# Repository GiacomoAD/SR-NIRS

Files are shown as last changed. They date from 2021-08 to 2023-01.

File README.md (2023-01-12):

# SR-NIRS
> Started on Jan/2021

SR-NIRS is a project to develop a low cost, portable, Spatially Resolved Near-Infrared Spectroscopy embedded system. Currently, the project is based on ESP-32 microcontroller.

The goal is to be able to monitor Tissue Oxygenation Index (TOI) from the forearm muscle during arm arterial occlusion experiment in a real time application.

The project also includes the development of a *Python GUI* to interact with the system.

*Undergraduate Final Project*

## Python GUI

This system was developed along with a Python GUI to enable wireless (currently Bluetooth) communication and data logging, as well as user monitoring of the incoming NIRS signal.

****

### Setup - Python Virtual Environment  

**This step, even though recommended, is not required. You can skip to Python Requirements sections if you wish.**

First of all, it is recommended to create a Python Virtual Environment. This can be done through python's embedded  (v. 3.4+) module called **venv**:

```
python -m venv [directory]
``` 

Then, the environment should be activated through:  
- ### Windows  
``` 
[directory]\Scripts\activate.bat
```

- ### Linux or MacOS  
```
source [directory]/bin/activate 
``` 

[More information on python virtual environments can be found here.](https://python.land/virtual-environments/virtualenv)

### Setup - Python Requirements

All of the required packages are included on **_requirements.txt_** file, inside **_GUI_** folder.  

These requirements can be installed through python's **pip** module, as it follows:

```
pip install -r requirements.txt
``` 

### Running GUI

To run the system GUI, the **_main.py_** script should be executed:
```
python main.py
``` 

***
## Documentation

The documentation will be in included in this repository as the project progresses.

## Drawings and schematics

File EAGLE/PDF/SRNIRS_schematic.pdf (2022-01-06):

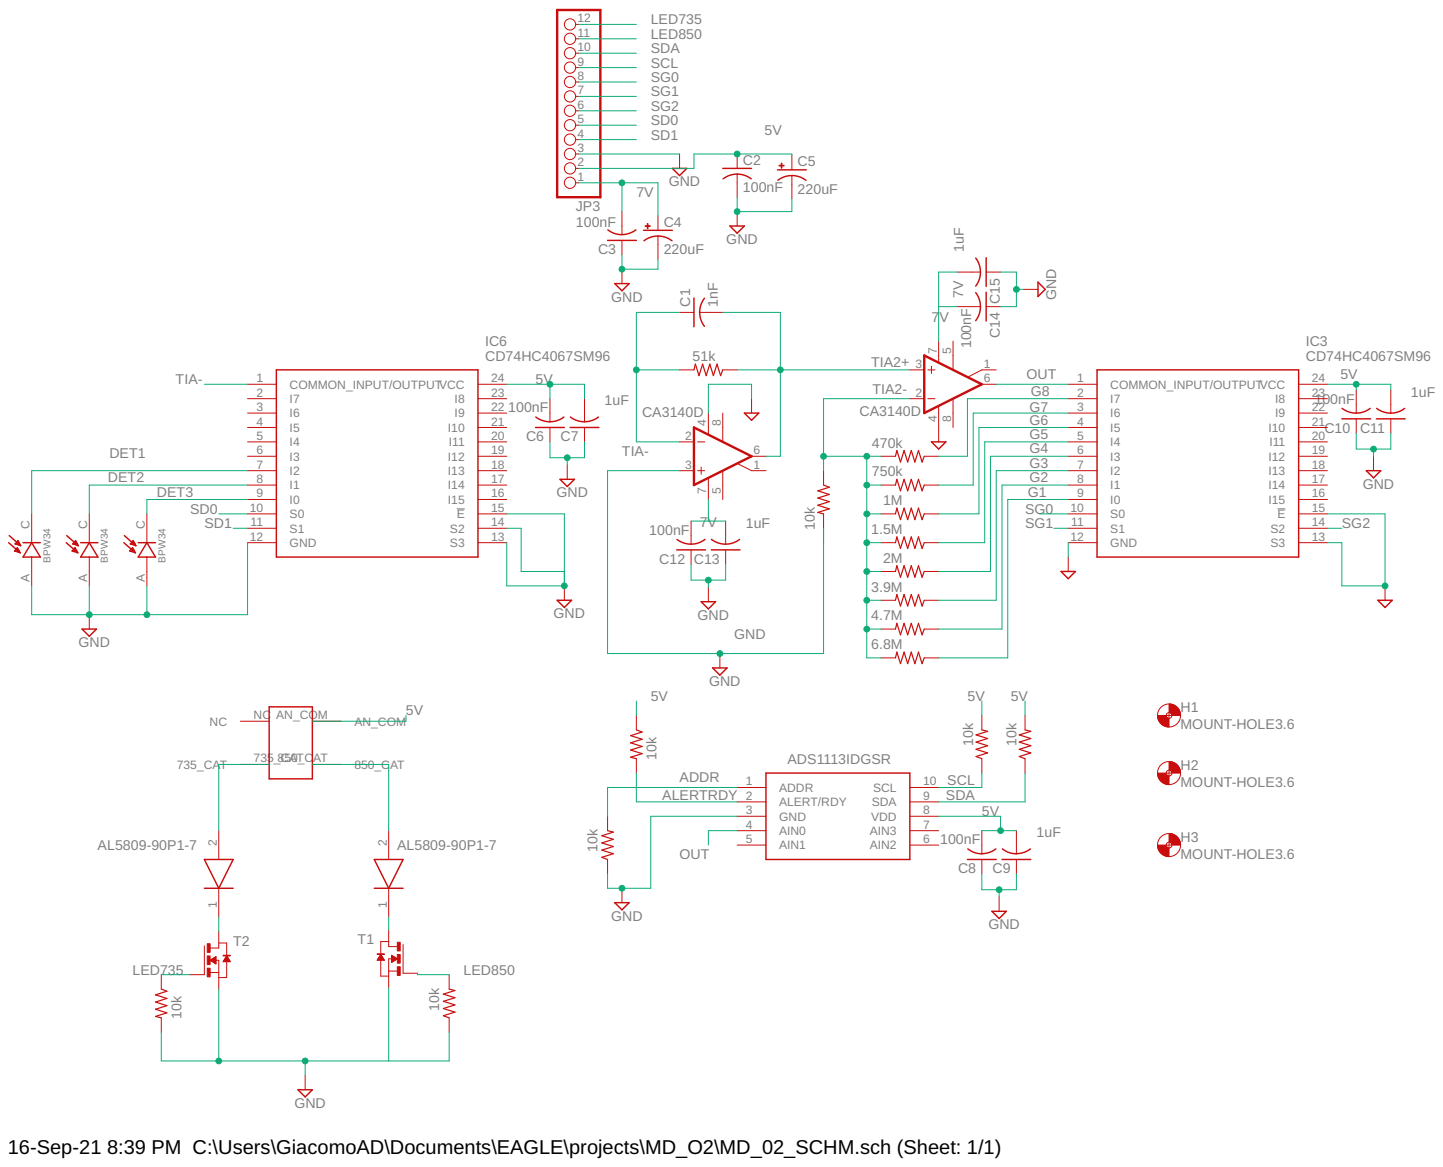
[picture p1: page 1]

16-Sep-21 8:39 PM C:\Users\GiacomoAD\Documents\EAGLE\projects\MD_O2\MD_02_SCHM.sch (Sheet: 1/1)

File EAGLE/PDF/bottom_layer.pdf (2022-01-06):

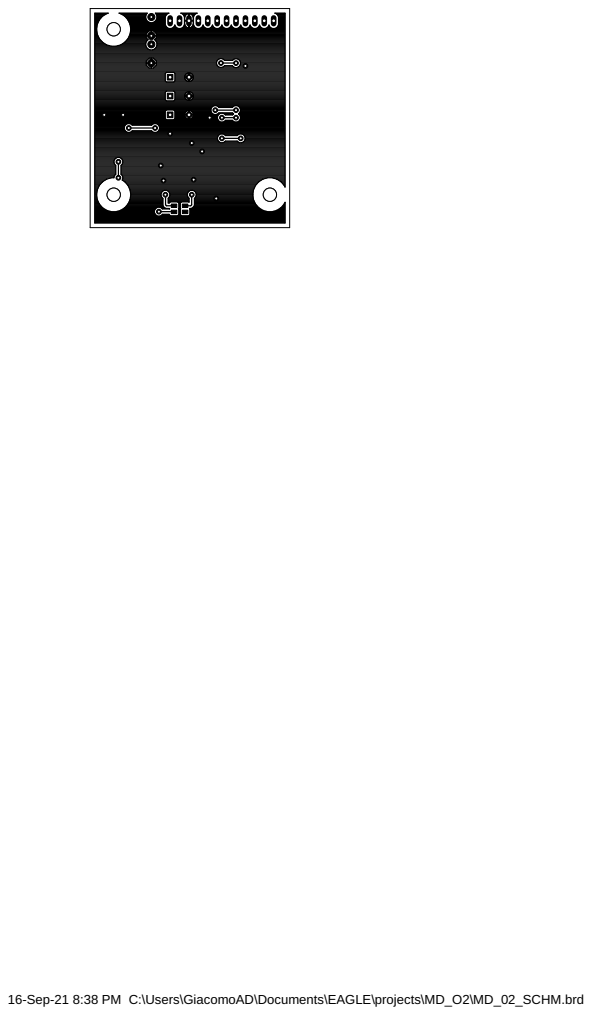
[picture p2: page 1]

16-Sep-21 8:38 PM C:\Users\GiacomoAD\Documents\EAGLE\projects\MD_O2\MD_02_SCHM.brd

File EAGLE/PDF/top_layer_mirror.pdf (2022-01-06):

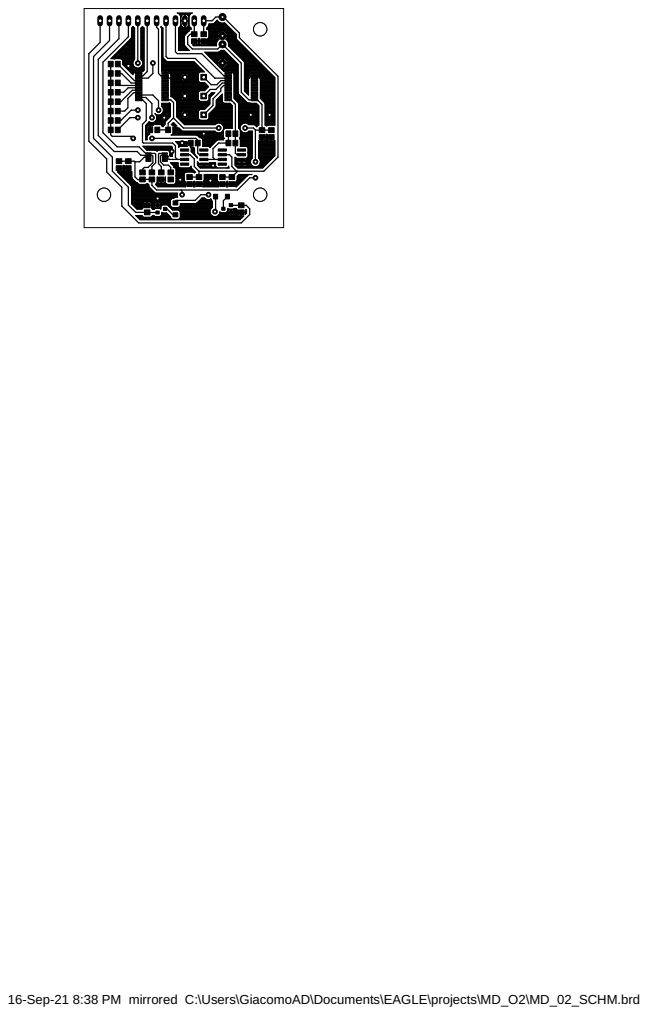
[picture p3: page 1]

16-Sep-21 8:38 PM mirrored C:\Users\GiacomoAD\Documents\EAGLE\projects\MD_O2\MD_02_SCHM.brd

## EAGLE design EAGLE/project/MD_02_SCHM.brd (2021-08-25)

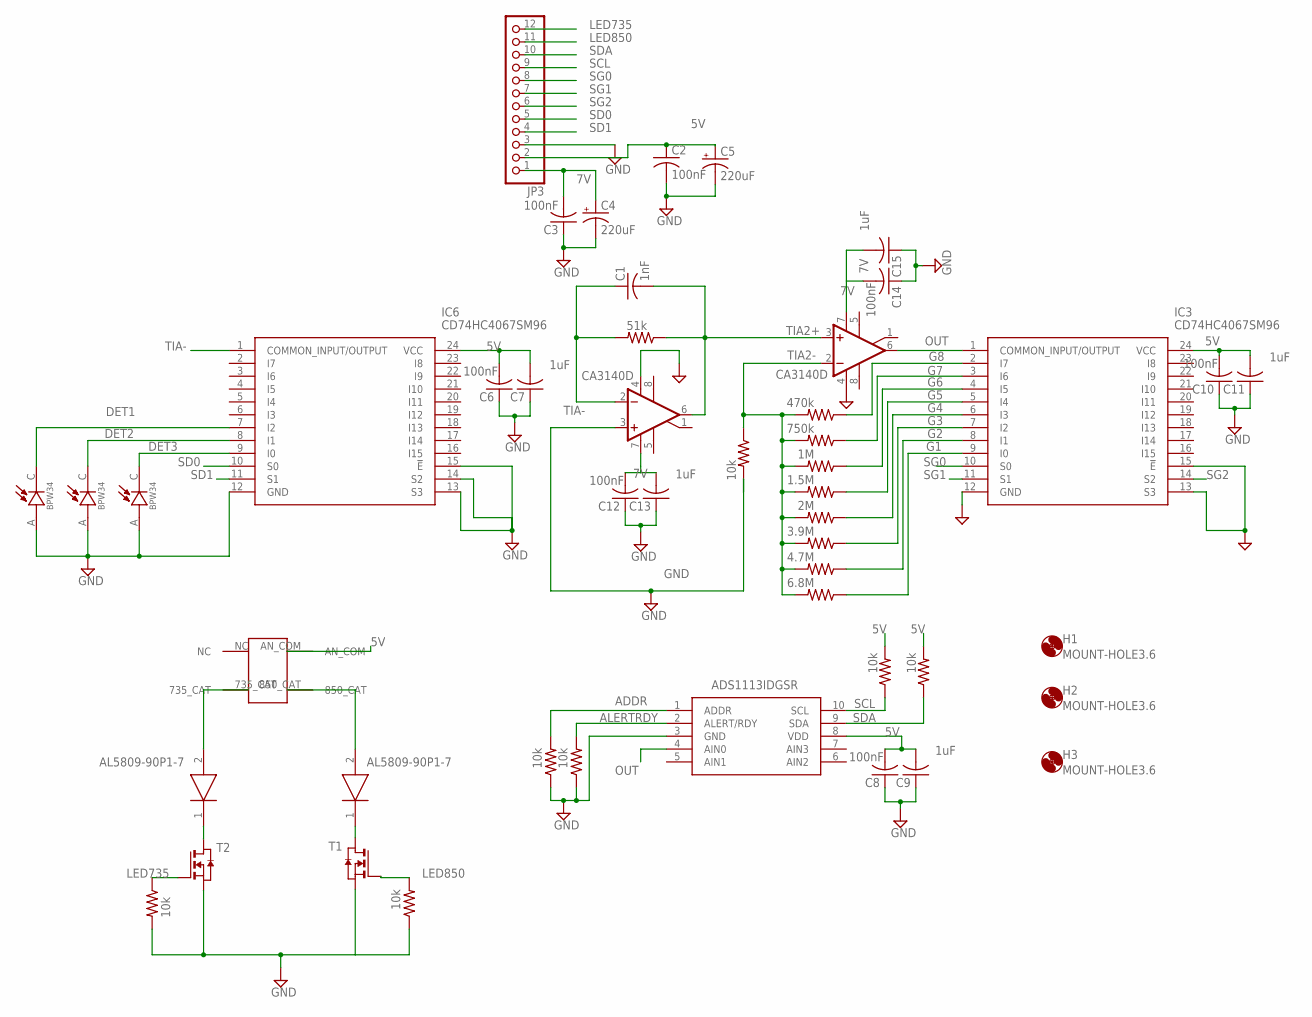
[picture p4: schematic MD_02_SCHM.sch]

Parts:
C1: 1nF; C0805
C2, C3, C6, C8, C10, C12, C14: 100nF; C0805
C4, C5: 220uF; E5-6
C7, C9, C11, C13, C15: 1uF; C0805
D1, D5: AL5809-90P1-7; SODFL3718X100N
D2, D3, D4: BPW34; DIO_BPW34
H1, H2, H3: MOUNT-HOLE3.6; 3,6
IC1, IC2: CA3140D; SO08
IC3, IC6: CD74HC4067SM96; SOP65P780X200-24N
IC5: ADS1113IDGSR; SOP50P490X110-10N
JP3: PINHD-1X12; 1X12
R1: 51k; R0805
R2, R11, R12, R13, R14, R15, R16: 10k; R0805
R3: 470k; R0805
R4: 750k; R0805
R5: 1M; R0805
R6: 1.5M; R0805
R7: 2M; R0805
R8: 3.9M; R0805
R9: 4.7M; R0805
R10: 6.8M; R0805
T1, T2: NMOSSOT23; SOT-23
U$1: SMT735D_850D

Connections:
5V: C2.1, C5.+, C6.2, C7.2, C8.2, C9.2, C10.2, C11.2, IC3.24 (VCC), IC5.8 (VDD), IC6.24 (VCC), JP3.2, R13.2, R14.2, U$1.AN_COM
7V: C3.2, C4.+, C12.2, C13.2, C14.2, C15.2, IC1.7 (V+), IC2.7 (V+), JP3.1
ADDR: IC5.1 (ADDR), R11.2
ALERTRDY: IC5.2 (ALERT/RDY), R12.2
DET1: D2.C, IC6.7 (I2)
DET2: D3.C, IC6.8 (I1)
DET3: D4.C, IC6.9 (I0)
G1: IC3.9 (I0), R10.1
G2: IC3.8 (I1), R9.1
G3: IC3.7 (I2), R8.1
G4: IC3.6 (I3), R7.1
G5: IC3.5 (I4), R6.1
G6: IC3.4 (I5), R5.1
G7: IC3.3 (I6), R4.1
G8: IC3.2 (I7), R3.1
GND: C2.2, C3.1, C4.-, C5.-, C6.1, C7.1, C8.1, C9.1, C10.1, C11.1, C12.1, C13.1, C14.1, C15.1, D2.A, D3.A, D4.A, IC1.3 (+IN), IC1.4 (V-), IC2.4 (V-), IC3.12 (GND), IC3.13 (S3), IC3.15 (!E), IC5.3 (GND), IC6.12 (GND), IC6.13 (S3), IC6.14 (S2), IC6.15 (!E), JP3.3, R2.2, R11.1, R12.1, R15.2, R16.1, T1.2 (S), T2.2 (S)
LED735: JP3.12, R15.1, T2.3 (G)
LED850: JP3.11, R16.2, T1.3 (G)
unnamed: D5.1 (K), T2.1 (D)
unnamed: D1.1 (K), T1.1 (D)
unnamed: D1.2 (A), U$1.850_CAT
unnamed: D5.2 (A), U$1.735_CAT
OUT: IC2.6 (OUT), IC3.1 (COMMON_INPUT/OUTPUT), IC5.4 (AIN0)
SCL: IC5.10 (SCL), JP3.9, R13.1
SD0: IC6.10 (S0), JP3.5
SD1: IC6.11 (S1), JP3.4
SDA: IC5.9 (SDA), JP3.10, R14.1
SG0: IC3.10 (S0), JP3.8
SG1: IC3.11 (S1), JP3.7
SG2: IC3.14 (S2), JP3.6
TIA2+: C1.2, IC1.6 (OUT), IC2.3 (+IN), R1.1
TIA2-: IC2.2 (-IN), R2.1, R3.2, R4.2, R5.2, R6.2, R7.2, R8.2, R9.2, R10.2
TIA-: C1.1, IC1.2 (-IN), IC6.1 (COMMON_INPUT/OUTPUT), R1.2

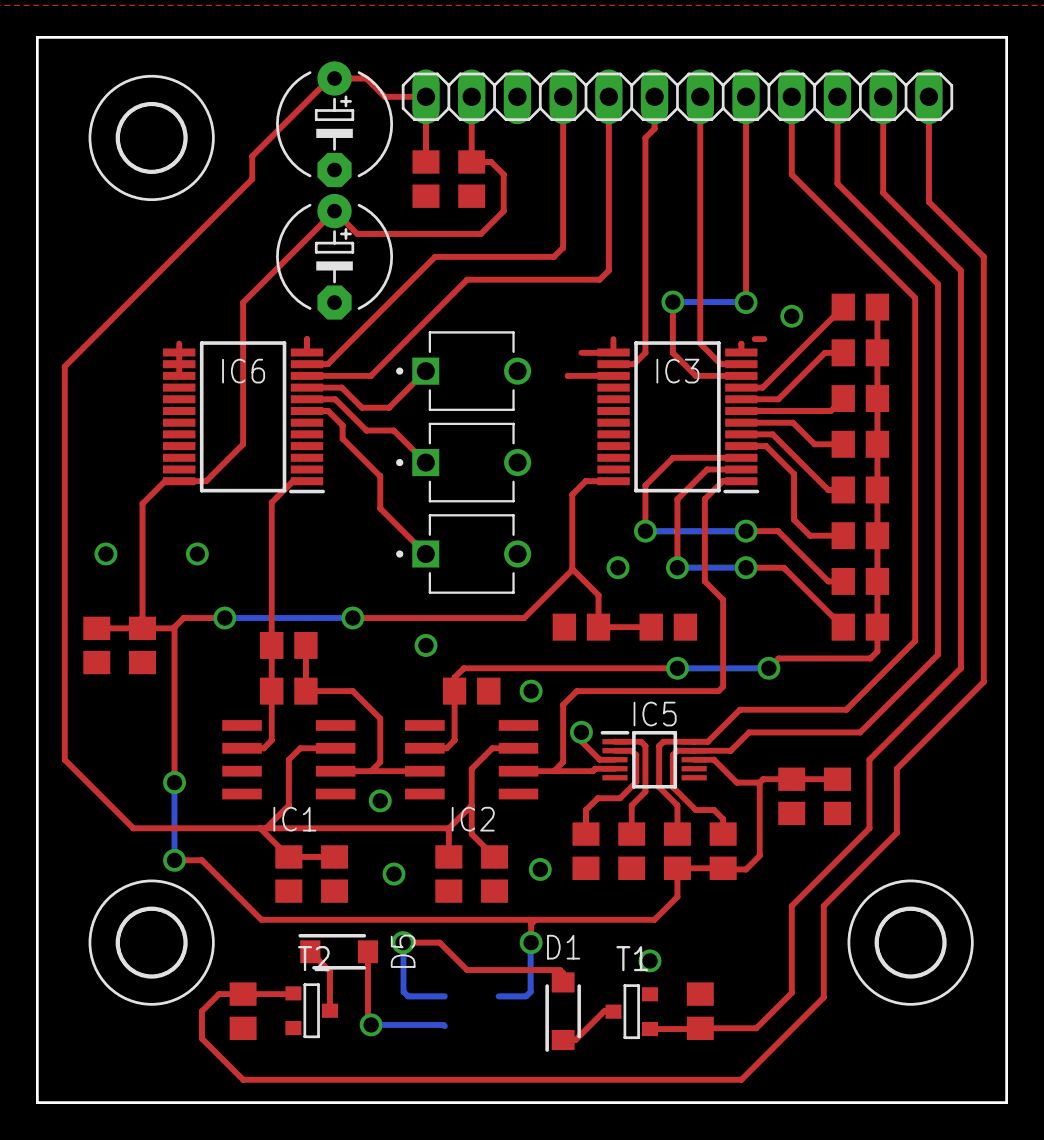
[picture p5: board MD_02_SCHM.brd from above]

Board: 2 copper layers, 53.8 x 59.2 mm, 48 parts (1 on the bottom side), 33 nets.

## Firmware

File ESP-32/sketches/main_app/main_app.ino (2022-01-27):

/* ***************************************************************** */
/* File name:        main_app.ino                                    */
/* File description: SR-NIRS sensor main app                         */
/* Author name:      Giacomo Dollevedo                               */
/* Creation date:    30Jun2021                                       */
/* Revision date:    26Jan2022                                       */
/* ***************************************************************** */

#include <Adafruit_ADS1X15.h>
#include <Wire.h>

#include <SRTimer.h>
#include <SRsensor.h>
#include <SRBluetooth.h>
#include <SRPressure.h>

/*SET DEBUG TO 1 TO ENABLE SERIAL MONITOR PRINTS*/
#define DEBUG 0

/*SET CALIBRATION TO 1 TO ENABLE AUTO-GAIN CHANGE*/
#define CALIBRATION 1
#define N_GAIN 8
#define MEANVAL 1
#define N_DET 3
#define MIDRANGE 18000L

/*DATA ACQUISITION FREQUENCY*/
#define FREQUENCY 50

/*BLUETOOTH MESSAGE PACKET*/
#define MAX_SIZE 16384
#define PACKET_SIZE 150

/*IMPORTED CLASSES OBJECTS*/
SRTimer timer;       // ESP-32 timer
SRSensor NIRSsensor;    // NIRS Sensor
SRBluetooth NIRSBt;     // Bluetooth comm
SRPressure NIRSpressure; // Pressure sensor and Sphymomanometer control

/************ TIMER VARIABLES ***********/
volatile unsigned char timer_flag = 0;

double initTime = 0.0; // Initial time
double cTime = 0.0;    // Current time
/******** END OF TIMER VARIABLES ********/

/************ SENSOR READ VARIABLES ************/

unsigned char sensorState = 0;

/******** END OF SENSOR READ VARIALES *********/

/************** SELF GAIN CHANGE VARIABLES *************/
unsigned char flagCalibrate = CALIBRATION;

int meanVal[N_GAIN];
int compare[N_GAIN];
int nRead = 0;
int compara = 0;
unsigned char currentChannel = 0;
unsigned char cDet = 0;
/********** END OF SELF GAIN VARIABLES *********/

/************** MEAN VALUE VARIABLES *************/

long means[N_DET][N_GAIN];
unsigned char currCh = 0;
unsigned char currGain = 0;
unsigned char flagMeans = MEANVAL;

/************** END OF MEAN VALUE VARIABLES *************/


/************** BLUETOOTH CONN VARIABLES *************/
int packets = 0; //
unsigned char packet_ready = 0; // Flag for ready to send packets
char *message_packet = (char *)calloc(MAX_SIZE, sizeof(char)); // Outgoing bluetooth message buffer

/********** END OF BLUETOOTH CONN VARIABLES **********/


/************** PRESSURE CONTROL VARIABLES *************/

unsigned char VOT_flag = 0;
unsigned char pump_flag = 0;
int VOT_start_time = 0;
/********** END OF PRESSURE CONTROL VARIABLES **********/


/*Timer interruption routine*/
void IRAM_ATTR timerInterrupt()
{

  timer_flag = 1;
  
}

void setup()
{

  //pinMode(4, OUTPUT);

  NIRSpressure.initPress();

  /* Initializing variables */
  for (int i = 0; i < N_GAIN; i++)
  {
    meanVal[i] = 0L;
    compare[i] = 0L;
    means[0][i] = 0L;
    means[1][i] = 0L;
    means[2][i] = 0L;
  }

  if (DEBUG)
  {
    Serial.begin(115200);
  }

  /* Toggling solenoid valve */
  NIRSpressure.toggleValve();

  /*Initializing NIRS Sensor object*/
  NIRSsensor.initSensor();

  /* Setting up timer frequency and interruption routine */
  timer.initTimer(6 * FREQUENCY, &timerInterrupt);

  /* Setting up Bluetooth Connection*/
  NIRSBt.initBt();

  /*Connecting to Bluetooth HC-05 antenna*/
  NIRSBt.connect();

  Wire.setClock(400000); // Setting I2C clock speed to 400 kHz

  /*Switching to IR to calibrate*/
  NIRSsensor.switchIR();
  
  timer.enableTimer();   // Enabling timer interruptions


  /*AUTO GAIN SETTING ROUTINE*/
  /*Finding mean read value for all channels + gains*/
  while(flagMeans)
    findMean();

  //digitalWrite(2, LOW);

  /*Finding which gain sets the value closer to the middle of the adc range*/
  while (flagCalibrate)
    calibrate();

  /*Creating configuration parameters message*/
  for(int j=0;j<N_DET;j++){
    for(int i=0;i<N_GAIN;i++){
      if(i==0){
        sprintf(message_packet, "%s#C\0", message_packet);
      }
      
      sprintf(message_packet, "%s%ld;\0", message_packet, means[j][i]);
    }
    
    sprintf(message_packet, "%s\n\0", message_packet);
  }

  //NIRSsensor.changeDetGain(5, 0);
  //NIRSsensor.changeDetGain(5, 1);
  //NIRSsensor.changeDetGain(4, 2);

  /*Sending configuration message over Bluetooth*/
  NIRSBt.sendGains(NIRSsensor.chGains); /*Auto gain settings*/
  delay(100);
  NIRSBt.sendData(message_packet); /*Sending all means by channel*/
  delay(100);
  message_packet[0] = '\0';

  NIRSpressure.setVotDuration(10);

  /*Resetting time variable to timestamp*/
  initTime = initTime = double(millis()) / 1000;
   
}

void loop()
{
  /* RUNS AT TIMER FREQUENCY*/
  if (timer_flag)
  {
    timer_flag = 0;

    /*Timestamping and reading pressure on the first data point*/
    if(sensorState == 0){
      cTime = getTimestamp();
      NIRSpressure.readPressure();
    }

    /*Reading from NIRS Sensor*/
    NIRSsensor.readState(sensorState);
    sensorState++;
    
  }

  processCommand(NIRSBt.readCommand());

  /*When the last sensor is read the outgoing message buffer is written*/
  if(sensorState == 6){
    sensorState = 0;
    /*Writing to Bluetooth outgoing buffer*/
    /*Message contains data structured as:*/
    /*time;IR[1];R[1];IR[2];R[2];IR[3];R[3]*/
    /*where 1, 2 and 3 are each respective channel*/
    sprintf(message_packet, "%s%.2f;%d;%d;%d;%d;%d;%d\n\0", message_packet, cTime, NIRSsensor.channelReadingsIR[0], NIRSsensor.channelReadingsR[0],
      NIRSsensor.channelReadingsIR[1], NIRSsensor.channelReadingsR[1], NIRSsensor.channelReadingsIR[2], NIRSsensor.channelReadingsR[2]);

    packets++; // adding to # of lines on packet

    /* If the packet ready to send */
    if(packets == PACKET_SIZE){
      sprintf(message_packet, "%s#P%03d\n\0", message_packet, NIRSpressure.getPressuremmHg());
      packet_ready = 1; // Flipping flag to send packets
      packets = 0;      // Resetting # of lines written
    }
  }

  /* If the packet ready to send */
  if(packet_ready){
    packet_ready = 0; // Resetting flag
    NIRSBt.sendData(message_packet);  // Sending outgoing buffer through Bluetooth
    //delay(10);
    message_packet[0] = '\0';
  }

  /*Processing VOT*/
  NIRSpressure.runVOT();
  
}

/* ************************************************************************************ */
/* Method's name:          findMean                                                     */ 
/* Description:            Finds every channel mean read value for each gain, based on  */
/*                         timer frequency                                              */
/*                                                                                      */
/* Entry parameters:       n/a                                                          */
/*                                                                                      */
/* Return parameters:      n/a                                                          */
/* ************************************************************************************ */
void findMean(){
  if(timer_flag){
    timer_flag = 0;

    means[currCh][currGain] += NIRSsensor.readSensor();
    nRead++;
    //digitalWrite(2, HIGH);

    if(nRead == 500){
      if(DEBUG){
        Serial.printf("%ld\t",means[currCh][currGain]);
      }
      
      means[currCh][currGain] = means[currCh][currGain]/nRead;

      if(DEBUG){
        Serial.printf("%ld\n",means[currCh][currGain]);
      }
      
      currGain++;
      
      
      if(currGain==N_GAIN){
        currGain = 0;
        currCh++;
        
      }

      else{
        NIRSsensor.changeGain(currGain);
      }
  
      if(currCh == N_DET){
        flagMeans = 0;
        nRead = 0;
        NIRSsensor.changeGain(0);
        NIRSsensor.changeCh(0);
      }

      else{
        NIRSsensor.changeCh(currCh);
        nRead = 0;
      }
      
    }
    
  }
}

/* ************************************************************************************ */
/* Method's name:          calibrate                                                    */ 
/* Description:            Uses mean values array to find set which gain will get the   */
/*                         sensor reading closer to the middle of adc range             */
/*                                                                                      */
/* Entry parameters:       n/a                                                          */
/*                                                                                      */
/* Return parameters:      n/a                                                          */
/* ************************************************************************************ */
void calibrate(){

  int testComp[N_DET][N_GAIN];

  unsigned char currGain = 0;
  int lastValue = 0;

  for(int i=0;i<N_DET;i++){
    for(int j=0;j<N_GAIN;j++){
      testComp[i][j] = means[i][j] - MIDRANGE;
    }
  }

  for(int i=0;i<N_DET;i++){
    currGain = 0;
    lastValue = 0;
    for(int j=0;j<N_GAIN;j++){
      
      if(j == 0){
        lastValue = testComp[i][j];
        currGain = j;
      }

      else{
        if (abs(testComp[i][j]) < abs(lastValue)){
          lastValue = testComp[i][j];
          currGain = j;
        }        
      }
    }
    
    NIRSsensor.changeDetGain(currGain, i);
    
  }
  
  flagCalibrate = 0;
  
}

/* ************************************************************************************ */
/* Method's name:          getTimestamp                                                 */ 
/* Description:            Calculate time based on the initTime variable                */
/*                                                                                      */
/* Entry parameters:       n/a                                                          */
/*                                                                                      */
/* Return parameters:      double -> time since the device began the measuring routine  */
/* ************************************************************************************ */
double getTimestamp(){
  return double(millis()) / 1000 - initTime;
}

/* ************************************************************************************ */
/* Method's name:          processCommand                                               */ 
/* Description:            Process incoming bluetooth commands                          */
/*                                                                                      */
/* Entry parameters:       char* bufferIn -> Array containing pre formatted command     */
/*                                                                                      */
/* Return parameters:      n/a                                                          */
/* ************************************************************************************ */
// TESTING
void processCommand(char* bufferIn){

  unsigned char pressure = 0;
  
  if(bufferIn[0] == '\0')
    return;
  
  else if(bufferIn[0] == '#'){
    switch(bufferIn[1]){
      case 'T':
        pressure = (100*(bufferIn[2]-48) + 10*(bufferIn[3]-48) + (bufferIn[4]-48));
        NIRSpressure.setPressureCap(pressure);
        NIRSpressure.setVotState(1);
        VOT_flag = 1;
        NIRSBt.clearBuffer();
        return;
      case 'S':
        VOT_flag = 0;
        NIRSBt.clearBuffer();
        return;
    }
  }

  else{
    return;
  }
  return;
}

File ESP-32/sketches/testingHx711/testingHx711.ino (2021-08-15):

/* ***************************************************************** */
/* File name:        testingHx711.ino                                */
/* File description: HX711 pressure reading test sketch              */
/* Author name:      Giacomo Dollevedo                               */
/* Creation date:    13Aug2021                                       */
/* Revision date:    15Aug2021                                       */
/* ***************************************************************** */

// CALIBRATION:
// P = 611030*(3.8184e-09 * READING - 0.0038)

#include <HX711.h>
#include <DroneTimer.h>

/*DATA ACQUISITION FREQUENCY*/
#define FREQUENCY 100

#define PCONST1 611030
#define PCONST2 0.0000000038184
#define PCONST3 0.0038

/*IMPORTED CLASSES OBJECTS*/
DroneTimer timer;       // ESP-32 timer

/************ TIMER VARIABLES ***********/
volatile unsigned char timer_flag = 0;

/******** END OF TIMER VARIABLES ********/


// HX711 circuit wiring
const int LOADCELL_DOUT_PIN = 17;
const int LOADCELL_SCK_PIN = 4;

HX711 sensorP;

/*Timer interruption routine*/
void IRAM_ATTR timerInterrupt()
{

  timer_flag = 1;
}

void setup()
{


  Serial.begin(115200);

  /* Setting up timer frequency and interruption routine */
  timer.initTimer(FREQUENCY, &timerInterrupt);

  timer.enableTimer();   // Enabling timer interruptions

  sensorP.begin(LOADCELL_DOUT_PIN, LOADCELL_SCK_PIN, 64);
   
}

void loop()
{
  /* RUNS AT TIMER FREQUENCY*/
  if (timer_flag)
  {
    timer_flag = 0;
    
    if (sensorP.is_ready()) {
      long reading = sensorP.read();
      //Serial.print("HX711 reading: ");
      int P = PCONST1*(PCONST2 * reading - PCONST3);
      Serial.println(P);
    } 
    else {
      //Serial.println("HX711 not found.");
      yield();
    }

    
  }

  

}

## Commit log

2021-07-14 Including new SRSensor class and main app. Now auto-gain calibration works with all 3 channels.
2021-07-29 Channel configuration combo box now working. Current settings displayed on configuration text field
2021-08-15 Pressure sensor reading through HX711 module testing sketch
2021-08-16 Adding EAGLE files
    [MD_02_SCHM.brd, MD_02_SCHM.sch, copper_bottom.gbr, copper_top.gbr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]
2021-08-17 Updating EAGLE files and top/bottom layers PDF
    [MD_02_SCHM.brd, MD_02_SCHM.sch, copper_bottom.gbr, copper_top.gbr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]
2021-08-25 Updated vias diameter and MUX footprint; Added GND vias; Polygon isolation changed to 24
    [MD_02_SCHM.brd, MD_02_SCHM.sch]
2021-08-25 Updating CAMOutputs to match updated project
    [copper_bottom.gbr, copper_top.gbr, drill_1_16.xln, gerber_job.gbrjob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]
2021-11-19 Adding PCB test sketch
2021-11-19 Add files via upload
    Adding PCB test sketch
2022-01-06 Adding SR Sensor schematic
2022-01-26 Main now runs both sensor reading and VOT
2022-01-27 Allowing for user VOT pressure input and sending arm cuff pressure back to GUI
2022-01-27 Added pressure input and display on monitoring tab
2022-01-27 Changes to allow pressure input from user and pressure display
2022-01-27 Will not display negative pressure values
